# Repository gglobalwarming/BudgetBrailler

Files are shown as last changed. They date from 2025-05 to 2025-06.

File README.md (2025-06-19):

# BudgetBrailler
Open source, open hardware, low-cost electric brailler. This project is a work in progress, although I have produced (mostly) working prototypes which make very nice braille dots. I am a biologist not an engineer of any sort so I'm sure there are many improvements to be made. Any feedback to improve the design would be appreciated!  

## Introduction
Braillers (aka Braille typewriters) are used by Blind or Visually Impaired persons to produce written text that can be "read" by touch based on patterns of dots. These devices can range from ~$800 for a mechanical Perkins Brailler to thousands of dollars for electric braillers. Having built several 3D printers from kits I wanted to see if I could design a low-cost brailler for a similar price to an entry level 3D printer. The  basic functional design is a set of rollers turned by a stepper motor to feed paper in and out, a toolhead on a linear rail driven by a stepper motor through a belt to move across lines of the paper, a linear actuator to imprint the dots on the page, and a keyboard for user input.  

## Design Goals
* The embosser should cost $100-200. My original inspiration for this project was that if you can buy or build a capable 3D printer for that price, you should be able to do the same with a braille embosser.  
* The embosser should be open source and open hardware.  
* The embosser should be entirely 3D printed or made with off-the-shelf components.  
* The embosser should be simple. There should be as few parts as possible and, except for the electronics, no complex mechanisms.  
* The embosser should have an optional case to protect the user and the embosser.  
* The embosser should be well documented. This includes a bill of materials, detailed instructions, code, wiring diagrams, and stl and CAD files for all printed parts.  

## Limitations
* Custom keyboard  
* Feeding paper is imprecise  
* Manually aligning first line on page required  
* Printing parts requires 256mm print bed  
* Long term durability not tested  
* Very little auditory feedback  
* Manual wiring and crimping needed
* No screen for high vision users

## Future Improvements:
* Implement user feedback. Please let me know any problems or suggestions you have!  
* Learn FreeCAD and remake all the 3D printed parts to move away from SolidWorks  
* Write code to allow the embosser to accept braille ASCII files to print  
* Implement QWERTY keyboard compatibility  
* Redesign custom keyboard to have its own microcontroller and memory  
* Allow keyboard to be used separately as a note taker then later connected for printing  
* Implement more auditory feedback from embosser  
* Detect when paper reaches the print line  
* Improve paper feeding more generally  
* Make 3D printable gears as an option  
* Search for alternative electronics which are simpler, less expensive, or more reliable  
* Design PCBs to reduce wiring complexity  
* Design alternate print heads to make different size dots
* Invert printing so that braille can be read right-side up without removing paper
* Add optical snsor to auto-align page for first line printing  
* Test different linear actuators  

## Similar Projects
There are several similar open source braillers, although they are directed at printing from files rather than being used like a typewriter. The top two are linked below:  
[BrailleRap](https://www.braillerap.org/en/)  
[OpenBraille](https://github.com/carloscamposalcocer/OpenBraille)

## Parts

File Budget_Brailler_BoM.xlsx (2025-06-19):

Name | Other Name/Notes | Quantity | Cost/Unit | Cost | Link
Total |  |  |  | 185.4533333
3D Printing |  |  |  | 30
Filament | ~1kg PLA/PETG/ABS, ~15g TPU | 1.5 | 20 | 30
Electronics |  |  |  | 81.63333333
Buck Converter | LM2596 | 1 | 1.3 | 1.3 | https://www.amazon.com/gp/product/B0DBVWQGZL/ref=ppx_yo_dt_b_asin_title_o00_s01?ie=UTF8&psc=1
Stepper Motor | XY42STH34-0354A | 2 | 14 | 28 | https://www.adafruit.com/product/324
NC End Stop | ThTRht B0CB85485W | 1 | 0.2 | 0.2 | https://www.amazon.com/dp/B0CB85485W?ref=ppx_yo2ov_dt_b_fed_asin_title&th=1
Mosfet Driver | RFP30N06LE N-Channel Power MOSFET | 1 | 0.8 | 0.8 | https://www.adafruit.com/product/5648
S2 Mini | Adafruit MOSFET Driver - For Motors, Solenoids, LEDs, etc - STEMMA JST PH 2mm | 1 | 4 | 4 | https://www.amazon.com/dp/B0CKLGGNKY?ref=ppx_yo2ov_dt_b_fed_asin_title
Motor Drivers | TB6612 | 2 | 7 | 14 | https://www.adafruit.com/product/2448
12V Linear Actuator | TAU1040T-07 | 1 | 15 | 15 | https://www.adafruit.com/product/413
Perma-Proto Board | Perma-Proto Quarter-sized Breadboard PCB (better solutions likely exist, I am just using it for common ground/power) | 1 | 2.833333333 | 2.833333333 | https://www.adafruit.com/product/589
Power Jack | Panel Mount 2.1mm DC barrel jack | 1 | 3 | 3 | https://www.adafruit.com/product/610
Piezo Buzzer | PS1240 | 1 | 1.5 | 1.5 | https://www.adafruit.com/product/160
12V Power Supply | I'm currently using a 12V 5amp power supply with a 2.1mm barrel jack. I doubt this uses the full 5 amps so I will update this once I test that. | 1 | 10 | 10 | https://www.amazon.com/Facmogu-Transformers-100-240V-Converter-Available/dp/B0BYVK73BP
Wire | If you're doing your own wiring. |  |  | 1
Connectors / crimping tools | If you're wiring your own connectors you'll need the appropriate connectors and tools.
Keyboard |  |  |  | 19.6
1N4007 Diode |  | 14 | 0.15 | 2.1 | https://www.adafruit.com/product/1641
Keys | CherryMX size | 14 | 0.5 | 7 | https://www.adafruit.com/product/4955
Keycaps | CherryMX size | 14 | 0.5 | 7 | https://www.adafruit.com/product/4997
Switch Sockets | Kailh Switch Sockets for MX-compatible Mechanical Keys - 20 Pack | 14 | 0.25 | 3.5 | https://www.adafruit.com/product/4958
Motion |  |  |  | 49.22
Bearing | F695rs Bearings | 2 | 0.95 | 1.9 | https://www.amazon.com/dp/B09YLDL5WK?ref_=ppx_hzod_title_dt_b_fed_asin_title_1_4
Belt | 2GT-6 Width | 0.5 | 9 | 4.5 | https://www.amazon.com/dp/B0BVJSRD6F?ref=ppx_yo2ov_dt_b_fed_asin_title
Idler | 5mm Bore 20 Teeth Suitable for 6mm Belt | 1 | 1 | 1 | https://www.amazon.com/dp/B07J4JC2N7?ref=ppx_yo2ov_dt_b_fed_asin_title
250mm Linear Rail | MGN12 250mm Linear Rail Guide with MGN12H Linear Bearing Carriage Block | 1 | 18 | 18 | https://www.amazon.com/dp/B09QPP35N1?ref=ppx_yo2ov_dt_b_fed_asin_title
Pulley | GT2 Pulley 20 Teeth 5mm Bore | 1 | 1.32 | 1.32 | https://www.amazon.com/dp/B0CPYN865G?ref=ppx_yo2ov_dt_b_fed_asin_title
Linear Rod | 5mm x 300mm linear rod | 2 | 5 | 10 | https://www.amazon.com/dp/B0CXVB6G3D?ref=ppx_yo2ov_dt_b_fed_asin_title&th=1
Motor Gear | 32P 20T Pinion Gear Mod 0.8, 5mm shaft (ProtekRC PTK-8063 is the one I used) | 1 | 4.5 | 4.5 | https://www.amainhobbies.com/protek-rc-steel-32p-pinion-gear-w-3.17mm-reducer-sleeve-mod-.8-5mm-bore-20t-ptk-8063/p735082?v=704112&gad_source=1
Roller Gears | 32P 27T Pinion Gear Mod 0.8, 5mm bore (Traxxas 5647 are the ones I used) | 2 | 4 | 8 | https://www.amainhobbies.com/traxxas-32p-hardened-steel-pinion-gear-w-5mm-bore-27t-tra5647/p454505?v=746125
Fasteners | Note: I think all the amounts here are correct. Having spares will never hurt. |  |  | 5
M2 Screws | M2x10 minimum, M2x20 maximum. Exact length not critical | 6
M2x10 Self-Tapping Screws | Used for mounting the end stop | 2
M2 Nuts |  | 6
M3x8 Screws |  | 20
M3x12 Screws |  | 19
M3x18 Screws |  | 8
M3x25 Screws | Note: you can also use another M3x30 screw and an extra M3 nut in place of this screw | 1
M3x30 Screw |  | 6
M3 Nuts |  | 21
M5x16 Screw |  | 1
M5 Nut |  | 1

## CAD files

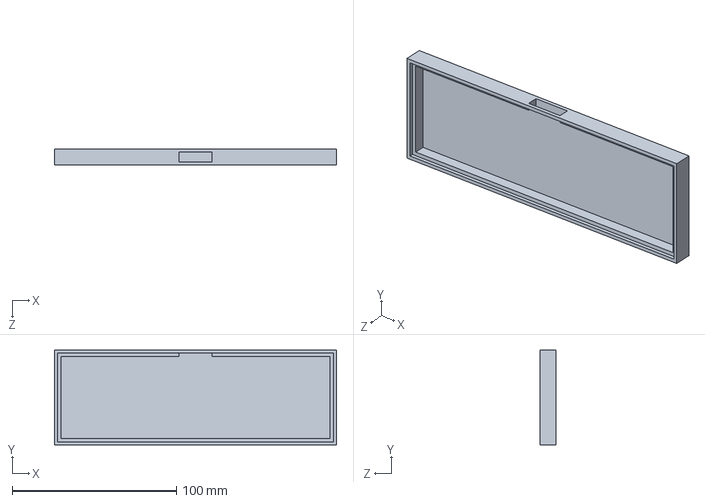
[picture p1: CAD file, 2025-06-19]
BB_Keyboard/BB_Keyboard_Bottom.SLDPRT
171.8 x 57.8 x 10.0 mm

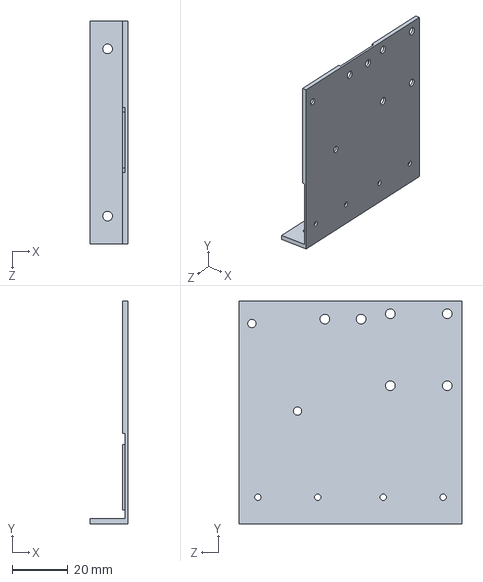
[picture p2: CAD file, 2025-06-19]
BudgetBrailler_Solidworks/BB_Electronics_Mount1.SLDPRT
13.6 x 80.0 x 80.0 mm

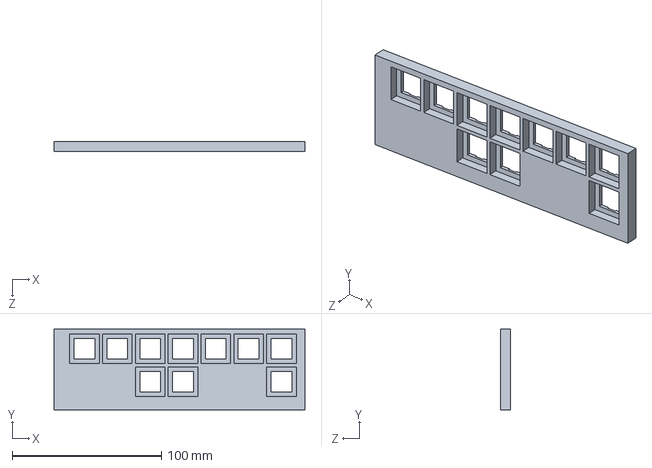
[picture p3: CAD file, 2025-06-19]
BB_Keyboard/BB_Keyboard_Top.SLDPRT
168.2 x 54.2 x 7.00 mm

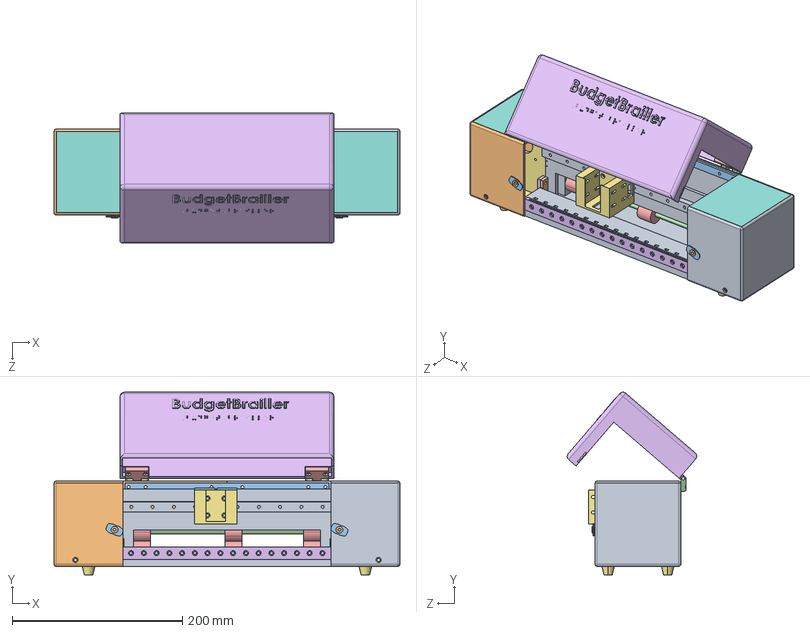
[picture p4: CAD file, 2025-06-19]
BudgetBrailler_Solidworks/BudgetBrailler.STEP
406.8 x 214.8 x 152.3 mm
BB_Middle
BB_Right_Side
BB_Left_Side
BB_Right_Casing
BB_Left_Casing
BB_Back_Brace
BB_Hinge_Outer x 2
BB_Hinge_Inner x 2
BB_Lid
BB_Carriage
BB_Belt_Clamp x 2
Linear_Rail
BB_Cam_Mount x 2
BB_Cam_Latch x 2
Rod_5x300mm x 2
BB_Roller_Gripper x 6
BB_Channel
BB_Foot x 4
BB_CB_Mount

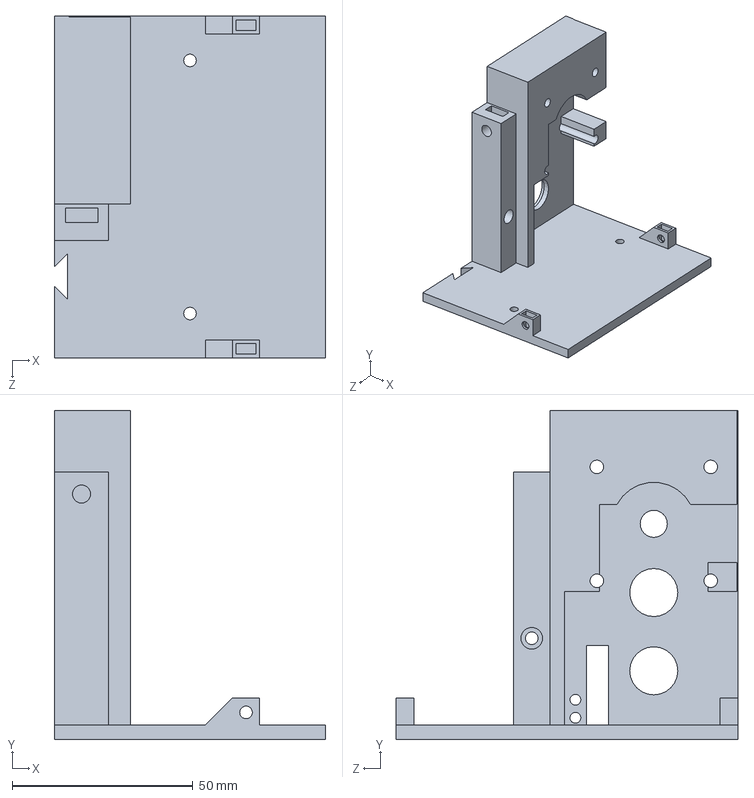
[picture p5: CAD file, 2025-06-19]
BudgetBrailler_Solidworks/BB_Right_Side.SLDPRT
75.0 x 91.0 x 94.5 mm

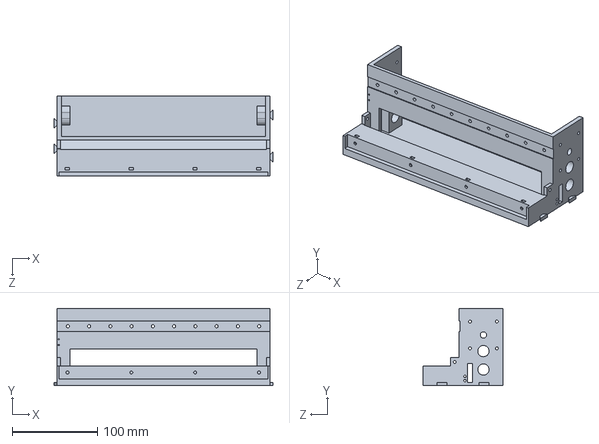
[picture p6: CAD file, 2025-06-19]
BudgetBrailler_Solidworks/BB_Middle.SLDPRT
257.5 x 91.0 x 94.5 mm

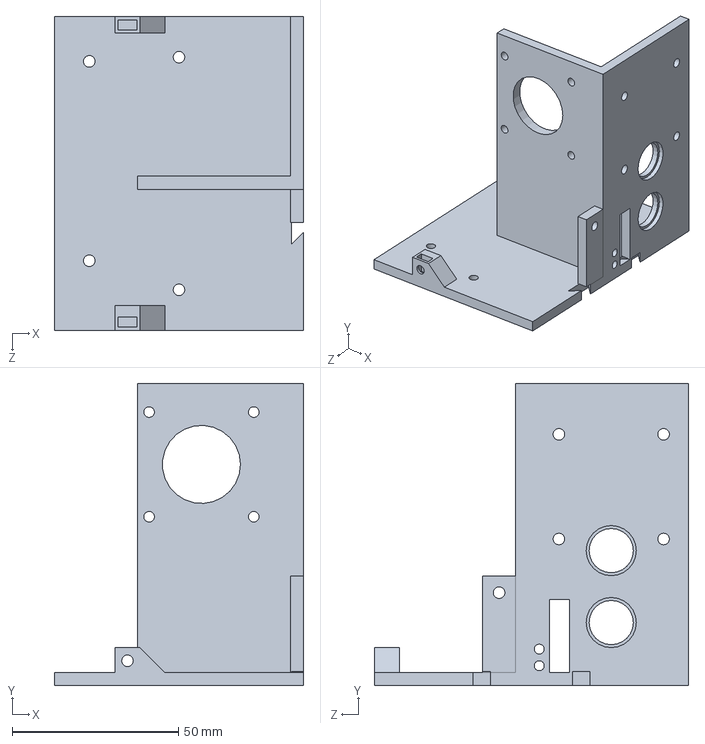
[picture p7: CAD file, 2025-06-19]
BudgetBrailler_Solidworks/BB_Left_Side.SLDPRT
75.0 x 91.0 x 94.5 mm

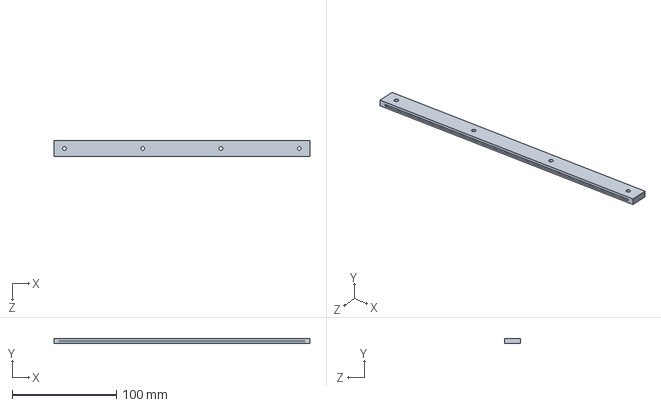
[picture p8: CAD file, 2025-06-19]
BudgetBrailler_Solidworks/BB_Channel.SLDPRT
245.4 x 5.00 x 15.0 mm

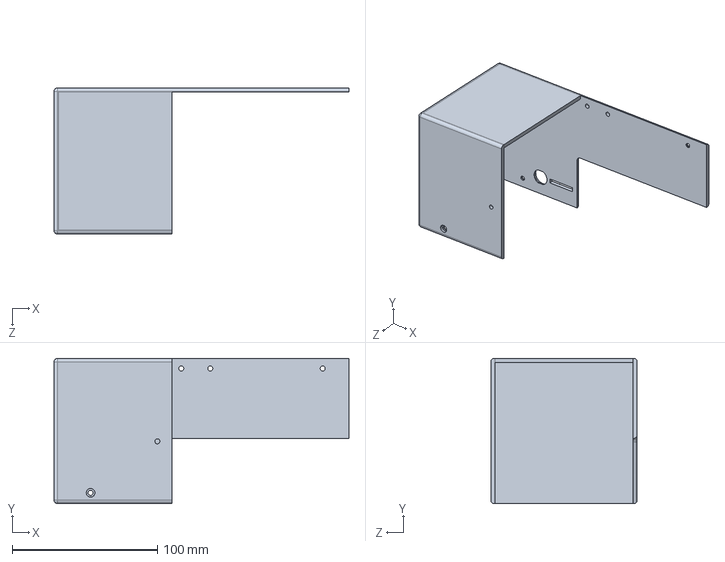
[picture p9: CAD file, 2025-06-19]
BudgetBrailler_Solidworks/BB_Left_Casing.SLDPRT
203.3 x 100.2 x 100.9 mm

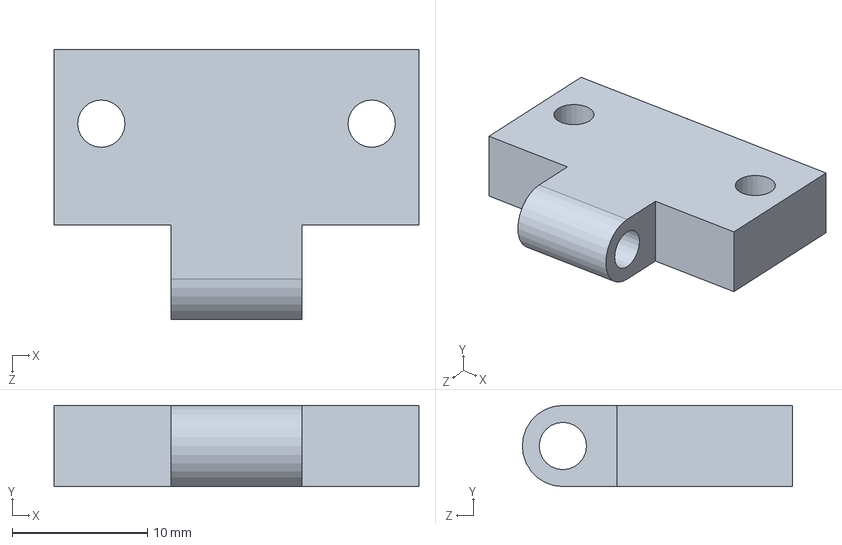
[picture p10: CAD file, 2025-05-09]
BudgetBrailler_Solidworks/BB_Hinge_Inner.SLDPRT
27.0 x 6.00 x 20.0 mm

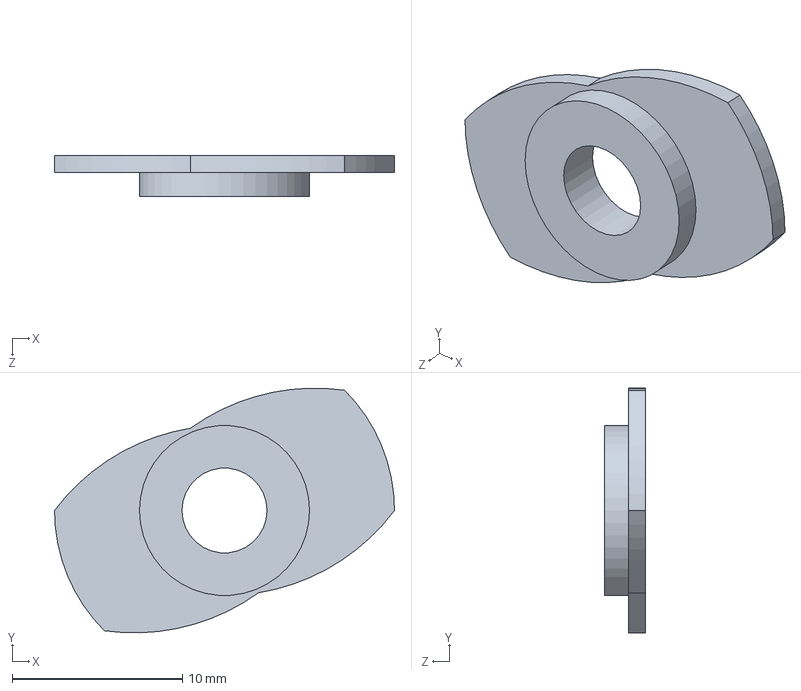
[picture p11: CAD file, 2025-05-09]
BudgetBrailler_Solidworks/BB_Cam_Latch.SLDPRT
20.0 x 14.4 x 2.40 mm

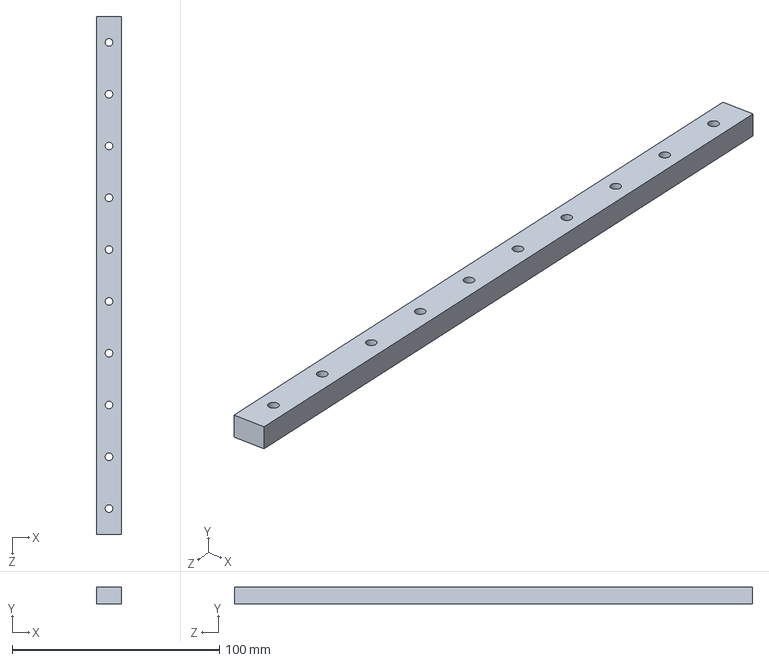
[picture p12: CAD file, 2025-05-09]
BudgetBrailler_Solidworks/Linear_Rail.SLDPRT
12.0 x 8.00 x 250.0 mm

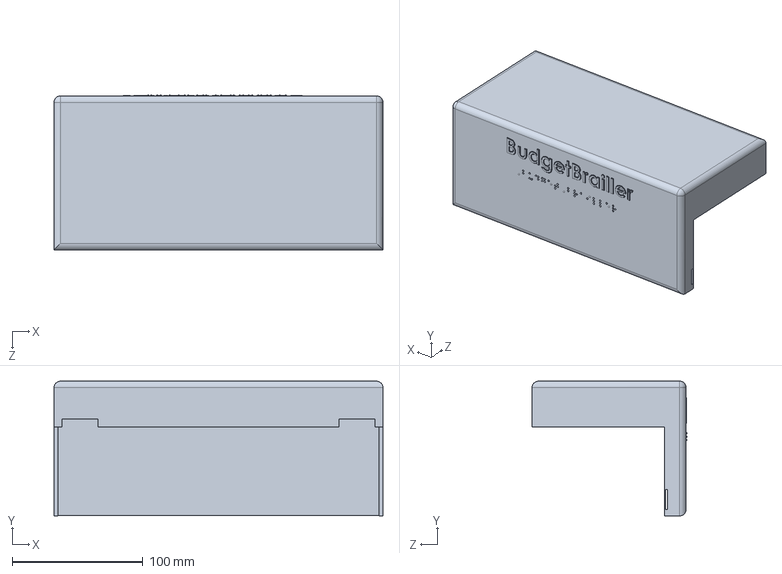
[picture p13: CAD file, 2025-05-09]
BudgetBrailler_Solidworks/BB_Lid.SLDPRT
251.4 x 103.0 x 118.4 mm

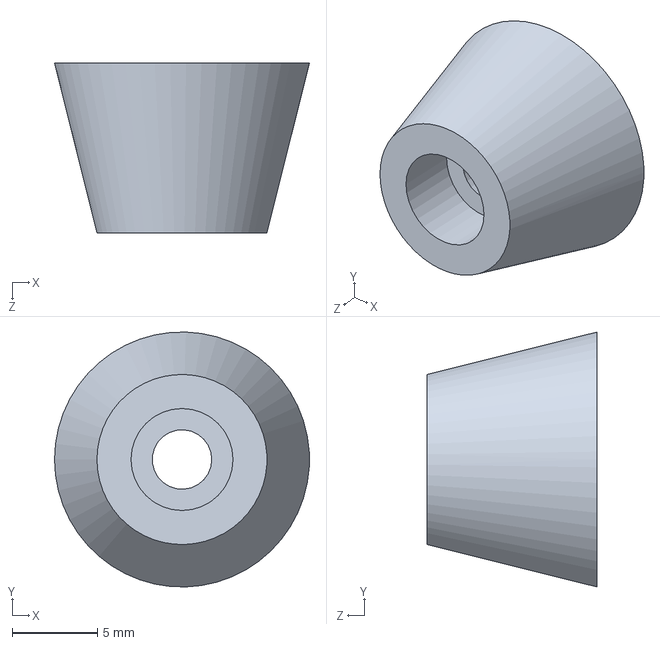
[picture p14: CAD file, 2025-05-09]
BudgetBrailler_Solidworks/BB_Foot.SLDPRT
15.0 x 15.0 x 10.0 mm

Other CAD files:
BudgetBrailler_Solidworks/BB_Belt_Clamp.SLDPRT
BudgetBrailler_Solidworks/BB_Roller_Gripper.SLDPRT
BudgetBrailler_Solidworks/BB_Carriage.SLDPRT
BudgetBrailler_Solidworks/BB_Hinge_Outer.SLDPRT
BB_Keyboard/BB_Keyboard_Bottom.STL
BB_Keyboard/BB_Keyboard_Top.STL
BudgetBrailler STLs/BB_Back_Brace.STL
BudgetBrailler STLs/BB_Belt_Clamp.STL
BudgetBrailler STLs/BB_CB_Mount.STL
BudgetBrailler STLs/BB_Cam_Latch.STL
BudgetBrailler STLs/BB_Cam_Mount.STL
BudgetBrailler STLs/BB_Carriage.STL
BudgetBrailler STLs/BB_Channel.STL
BudgetBrailler STLs/BB_Electronics_Mount1.STL
BudgetBrailler STLs/BB_Foot.STL
BudgetBrailler STLs/BB_Hinge_Inner.STL
BudgetBrailler STLs/BB_Hinge_Outer.STL
BudgetBrailler STLs/BB_Left_Casing.STL
BudgetBrailler STLs/BB_Left_Side.STL
BudgetBrailler STLs/BB_Lid.STL
BudgetBrailler STLs/BB_Middle.STL
BudgetBrailler STLs/BB_Right_Casing.STL
BudgetBrailler STLs/BB_Right_Side.STL
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

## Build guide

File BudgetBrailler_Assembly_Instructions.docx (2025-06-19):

BudgetBrailler Assembly Instructions

https://github.com/gglobalwarming/BudgetBrailler

NOTE: Assembly instructions are currently for a previous version. There have only been small changes, but I will remake the instructions soon with updated pictures, parts, and instructions.

Printed Parts:

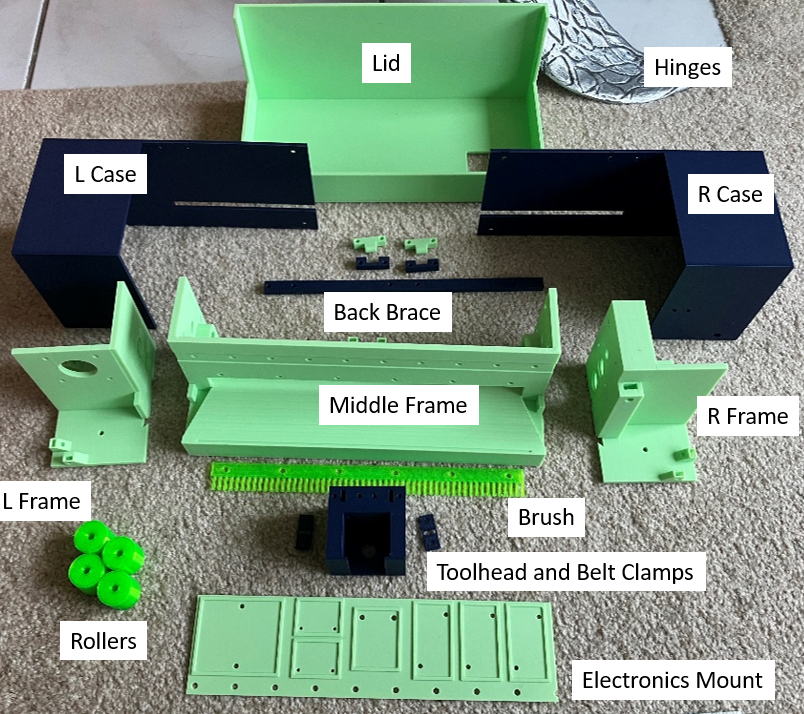
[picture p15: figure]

Parts to print in TPU:

- 4x Rollers: Cylinders 22mm in diameter and 20mm in length with a 5mm bore through the center. These are put on the linear rods and are used to grip the paper.
- 4x Feet: Conical pieces 10mm tall with 15mm and 10mm diameter ends a bore through the center for an M3 screw and nut. Used to reduce noise during printing and protect the surface the printer is on. Not present in the picture because I forgot to print them ahead of time.

Required parts printed in PLA/PETG:

Note: I printed mine out of PLA because I have been actively redesigning parts and wanted to more easily reprint parts as I iterated. As is always the case with FDM printing, PLA will be less durable and UV sensitive so ideally the parts should be printed from a different material (in this case PETG is probably the most sensible choice). Note: the “ramps” that are described below exist to allow printing of M3 nut mounts without supports. They do not serve any other function in the printer.

- 1x Left Frame: Contains the x-motor mount as well as spaces for the left bearings. Rectangular base 65mm wide by 95mm long. On the base are 4 ramped structures 15mm wide by 7.5mm long by 7.5mm with space for M3 nuts. These are used for mounting the case to the frame. Rising from the base is a backwards L-shaped wall 87mm tall with one leg near the center of the base and the other on the far-right side extending to the back. Near the top, the front wall has four holes for M3 screw and a larger 25mm hole in the middle. These holes are used to mount the x-axis motor and allow the shaft the pass through to the front of the embosser. On the right side of the L-wall near the top are four holes for M3 screw for connecting the left frame to the middle frame. Below that are two sets of holes ~15mm in diameter for the bearings. These wholes have a larger, shallower hole around a slightly smaller deeper hole to accommodate the shape of the bearings. Just in front of the L-wall on the right side is a raised piece with an M3 screw hole on it as another point to attach to the middle frame. On the bottom of the left frame on the right side are two ~10mm dovetail cutouts that connect to the middle frame. On the bottom are also two M3 screw holes for mounting the TPU feet.
- 1x Middle Frame:
- 1x Right Frame: Contains space for the roller motor as well as spaces for the left bearings and a mount for the belt idler. Close to a mirror image of the left frame with the following differences: No holes for an x-axis motor, additional hole in the center of the four screw holes that connect to the middle frame to provide space for the roller motor shaft, spacer extending around those same four screw holes to provide space between the roller motor and the wall, the piece holding the front screw hole to connect to the middle piece extends upward about 60mm where it has an M5 screw hole and space for an M5 nut to mount the belt idler.
- 1x Toolhead: Attached to the linear rail on the middle frame. Holds the linear actuator and move in the x-axis of the embosser. ~50mmm cube with a large cutout in the front/middle for the linear actuator. At the back is a cutout to fit onto the carriage of the linear rail as well as a cutout for the belts to pass through. Four M3 screw/nut holes go through the toolhead vertically near the back to mount the belt clamps as well as rectangular holes for the belt to pass through.
- 2x Belt Clamp: Attached to the top of the toolhead to hold the belts in place. Rectangular pieces 25mm by 10mm by 2mm with two holes for M3 screws and a rectangular hole for the belt to go through.
- 1x Electronics Mount: Attached to the middle frame behind middle wall and used to hold electronic components in place. Rectangular piece about 230mm by 55mm by 1mm with a row of 9 holes for M3 mounting screws at the bottom. On the front are a series of raised outlines for the various electronic components with holes for M3 or M2 screw to hold each part in place. From left to right (the largest outline should be on the far left): Solderable prototype board above the first three mounting screw holes, two motor drivers both above the fourth mounting screw hole, ESP-32 S2 Mini microcontroller above the fifth and sixth mounting screw holes, LM2596 buck converters for converting the 12V input power to the 5V needed to power the microcontroller above the seventh set of screw holes. To the right of these is 65mm of empty space which could be used in the future for mounting additional components.
- 1x Embosser: A 10mm diameter base, 3.5mm top cone with a small raised dot on one the small end of the cone the size of a braille dot and the other end of the cone hollow. Friction fits onto the end of the linear actuator with the hollow end and is used to emboss the braille dots. Not pictured because I forgot to print it ahead of time.
- 1x Keyboard Bottom: An open topped box 167mm by 53mm by 20mm with six screw and nut holes for M3 screws to hold the electronics and Keyboard Top to the bottom of the keyboard. Has a 2mm cutout on the top for the Keyboard Top to snap into place. Has a 20mm by 6mm hole at the back for cables to pass through.
- 1x Keyboard Top: 163mm by 63mm by 9mm box with two cutouts for M3 screws to connect to the Keyboard Bottom and 10 slots for MX Cherry keyboard keycaps.
- Left Case:
- Right Case: a mirror image of the left case.
- Lid:
- Back Brace:
- 2x Hinge Outer:
- 2x Hinge Inner:

Purchased Components:

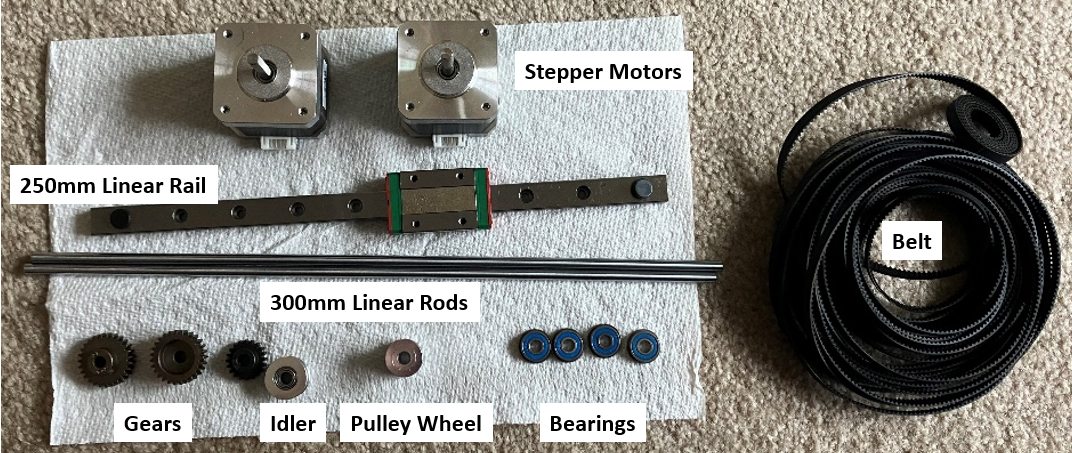
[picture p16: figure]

- 2x Stepper Motor: 42mm x 40mm stepper motors to drive the x-axis and rollers. Cube roughly 40mm/side. Near the bottom on one side face is a plug with six pins for plugging in a cable. On the top are four M3 screw holes for mounting the motor, a round 1mm by ~20mm raised ring with a 5mm shaft in the center. The shaft has one side flattened to allow a set screw to grip better.
- 1x 250mm Linear Rail: The toolhead will be mounted on the carriage of this linear rail to allow it to move on the x-axis. A metal rectangular piece 250mm by 5mm by 3mm with 10 holes for M3 mounting screws. On the a 40mm by 20mm rectangular carriage which slides along the rail. In the two outermost screw holes are rubber caps which prevent the carriage from sliding off and spilling the ball bearings inside it all over the place.
- 3x Gears: These gears come in two sizes. One is slightly smaller and will be attached to the roller motor shaft. The other two are slightly larger and will go on each of the two linear rods. The three gears will mesh in a vertical line in the order: Motor>Top Rod>Bottom Rod. Therefore, when the motor turns in one direction, the top rod will turn in the opposite direction and the bottom rod will turn in the same direction. For example: motor turning clockwise, top rod turning counterclockwise, bottom rod turning clockwise. Because the rollers on the top rod will be gripping the top of the paper and the bottom rod the bottom of the paper, the opposing directions of rotation will result in both rods pushing the paper in the same direction.
- 1x Idler: Placed on the opposite end of the linear rail from the x-axis motor and will allow the belt to loop back to the toolhead. A metal cylinder with a bearing in the middle and a 5mm bore. Around the outside of the cylinder are teeth to mesh with the belt.
- 1x Pulley Wheel: Attached to the x-axis motor to drive the belt. Metal cylinder with teeth on the outside to mesh with the belt. There are two holes 90° apart from one another on the rounded side for the threading of set screws to hold the pulley wheel on the motor shaft.
- 4x Bearings: Used to allow the rods to rotate freely while being held in place. Round metal pieces ~20mm in diameter with a 5mm bore. The center section can rotate freely.
- 1000mm (1m) Belt: Used to move the toolhead along the x-axis. 6mm wide plastic belt flat on one end and with teeth on the other. Embedded in the belt are strands of wire to provide added strength. Actual length used will be closer to 750mm.

Fasteners

M2 Screws (M2x10 minimum, M2x20 maximum) | 6
M2x10 Self-Tapping Screws | 2
M2 Nuts | 6
M3x8 Screws | 20
M3x12 Screws | 19
M3x18 Screws | 8
M3x25 Screws | 1
M3x30 Screw | 6
M3 Nuts | 21
M5x16 Screw | 1
M5 Nut | 1

Frame Assembly:

In this section we will assemble the main frame of the embosser. As part of the that assembly we will also mount most of the components to the frame.

1. Insert bearings into the holes on the sides of the Left and Right Frames. The fit should be tight and the bearings should snap securely into place. The bearings should sit roughly flush with the wall of the once they are inserted.

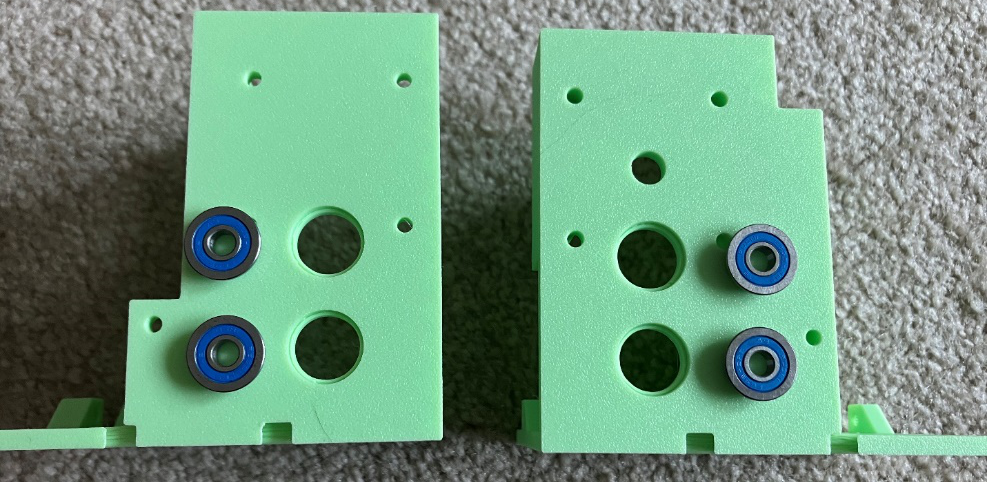
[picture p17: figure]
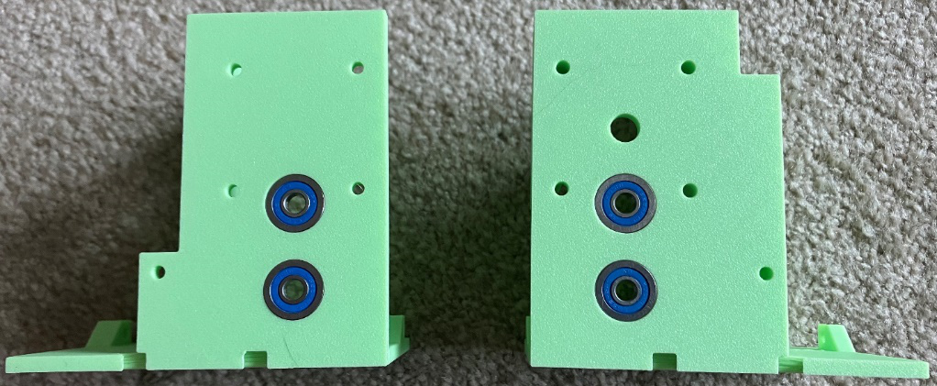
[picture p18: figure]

2. Connect the Left and Right Frames to the Middle Frame using the dovetails on the bottom. The wall running near the center of each of the frames should be colinear. If the walls are out of alignment you probably have the left and right segments swapped. The dovetails should be tight but can be removed if you made a mistake. The bottom of the frames do not need to be perfectly flush as connecting screw between the pieces will secure the frame.

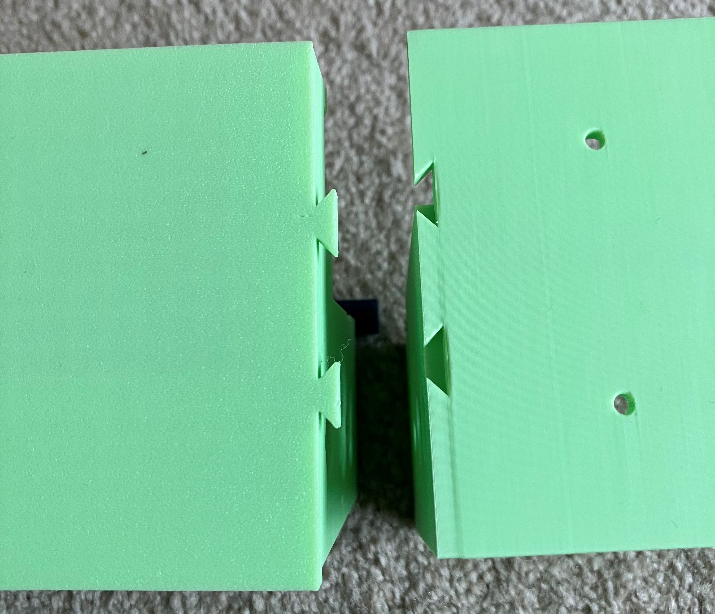
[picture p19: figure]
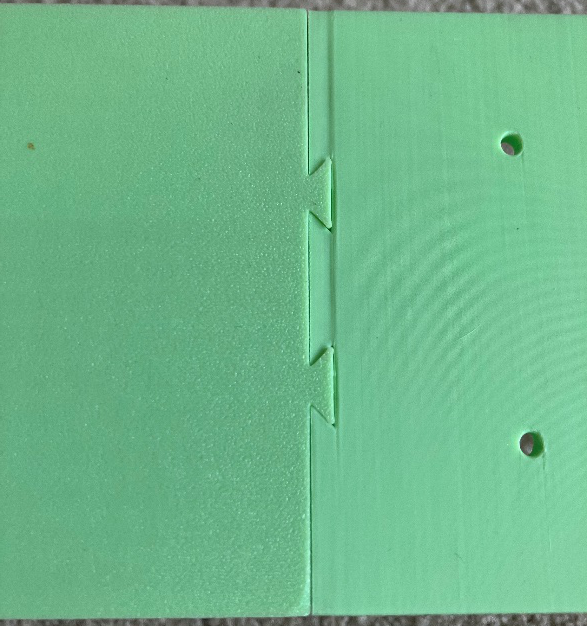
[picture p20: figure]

3. Attach the 3d printed feet to the bottom of the left and right frames with four M3x12 screws and four M3 nuts. There is space for a M3 nut to be trapped on the bottom side of the feet and a screw can be inserted from the top side of the frame.

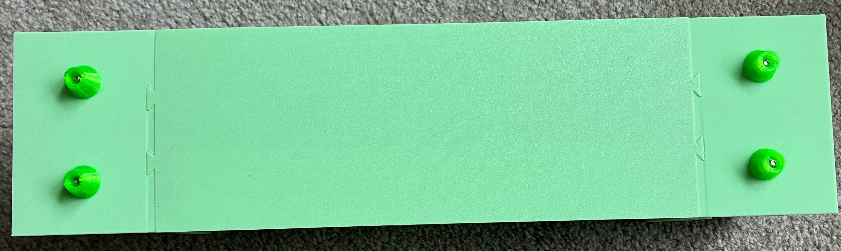
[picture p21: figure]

4. At the front of the frame, connect the Left Frame to the Middle Frame using the screw hole just in front of the middle wall using an M3x12 screw and an M3 nut.
5. At the front of the frame, connect the Right Frame to the Middle Frame using the screw hole just in front of the middle wall using an M3x25 screw and an M3 nut. Note: you can also use an M3x30 screw with an M3 nut put on by the head of the screw as a spacer. This reduces the number of different screws you need.
6. At the back of the frame, connect the Left Frame to the Middle Frame using the four screw holes on the parallel walls with four M3x12 screws and four M3 nuts

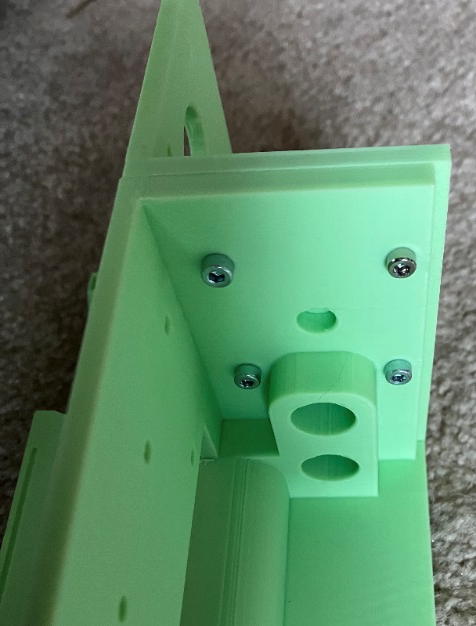
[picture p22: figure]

7. Attach the 32P 20T Mod 0.8, 5mm shaft Pinion Gear to one of the stepper motors by sliding it onto the shaft with the teeth farther from the motor body about 8mm from the end of the shaft. Align the set screw with the flat side of the shaft and tighten the screw. You should now be able to rotate the gear and shaft together without the pulley slipping. This will be the roller motor.
8. Orient the motor so the plug is oriented up. At the back of the frame, attach the roller motor to the top of the Right Frame (which will currently be on the left side of the frame since you are looking at it from the back) using four M3x30 screws. The screws will go into the four holes near the top on the left side (while looking at the frame from the back) of the Middle Frame, go through the thick wall on the Right Frame, and thread into the holes on the motor. Check to make sure the plug on the motor is still facing up. You may need to adjust the positioning of the pulley on the motor shaft. You can access the gear and its set screw from below. The gear should be close to the wall but ideally not touching the wall. The other gears will be larger so the exact placement of this gear is not critical to ensure that the gears mesh.

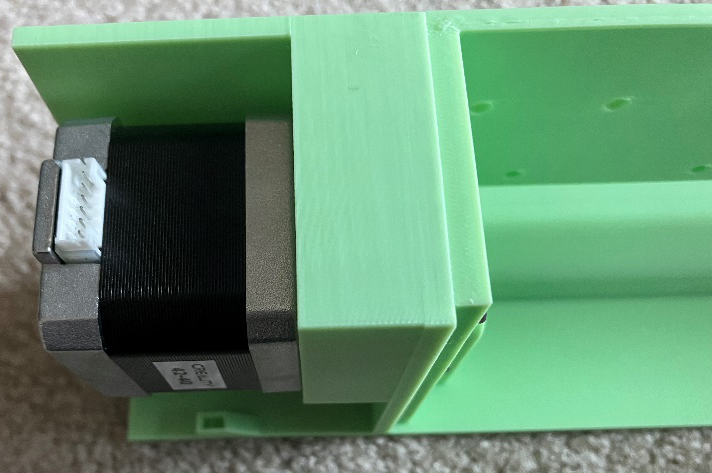
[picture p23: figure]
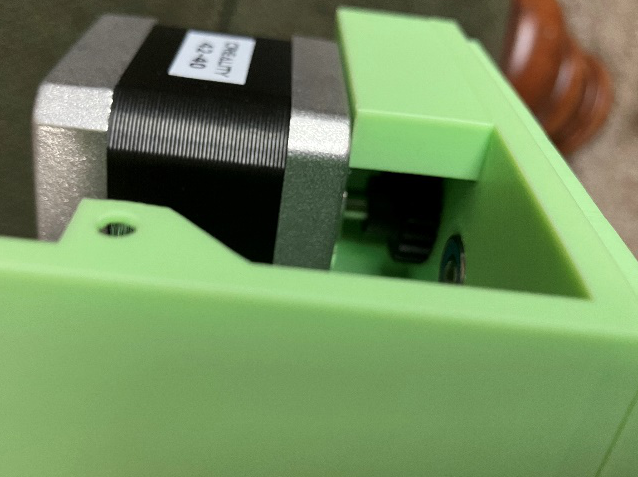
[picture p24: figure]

9. From the back of the frame, insert the linear rods through the bearing on the Left Frame (currently on the right side as we are viewing the back of the frame) and about halfway through the Middle Frame. Slide two roller grippers onto linear rods, ensuring that there is at least 20mm between the grippers and that there is at least 30mm of rod sticking past the leftmost gripper. Note: The grippers will be VERY tight on the rod. Starting with the top rod, slide the linear rods through the bearing on the Right Frame (currently on the left side as we are viewing the back of the frame) and put a 32P 27T Mod 0.8, 5mm shaft Pinion Gear on the left end of the rod flush against the Right Frame wall. Adjust the rod so the end is flush with the end of the gear then tighten the set screw on the gear. The top rod gear and the motor gear should mesh with a little bit of wiggle room. While holding the rod gear in place against the Right Frame wall, push the closes roller gripper toward the gear as far as it will go. Repeat with the farther gripper but moving it away from the gear to the far side of the Middle Frame. The top rod should now be able to rotate but not move from left to right. Attach the gear and adjust the roller grippers on the bottom rod in the same way you did for the top rod. The bottom rod gear should mesh with the gears on the top rod and when you turn one gear the other should move smoothly in the opposite direction. Try feeding some braille paper or an index card through the rollers by manually turning one of the rollers to ensure that both sets of rollers grip the paper. Note: regular printer paper will not work well as it is too thin and tends to crumple.

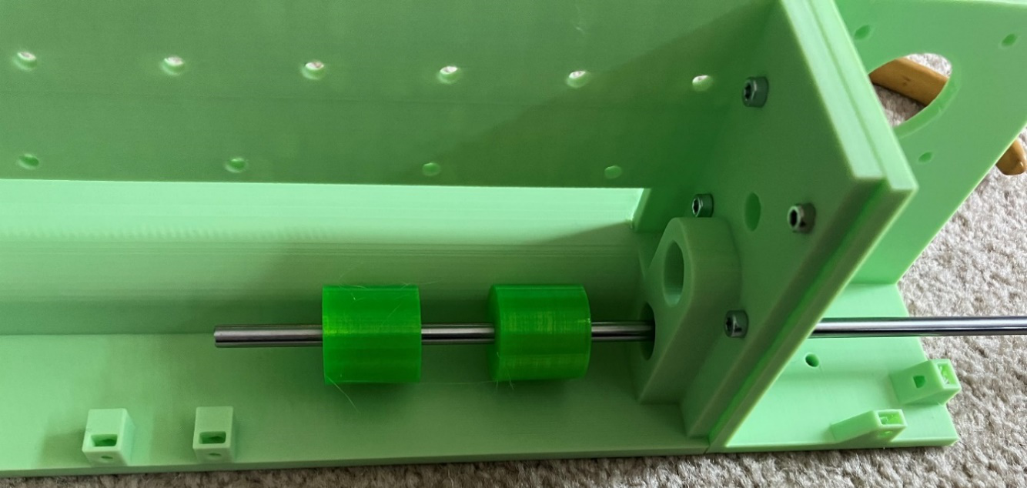
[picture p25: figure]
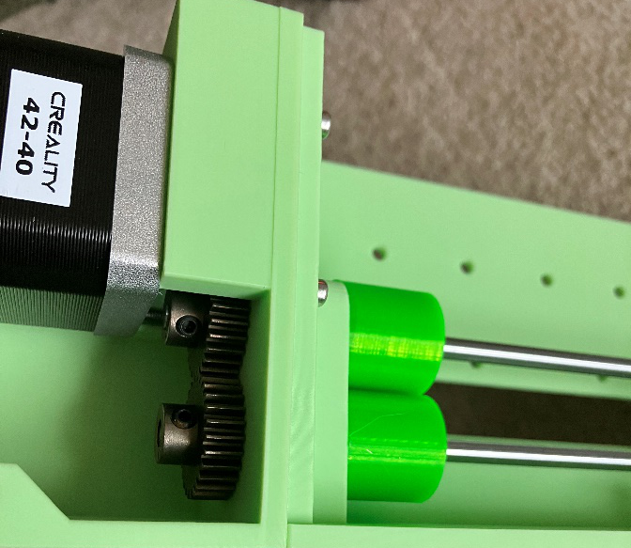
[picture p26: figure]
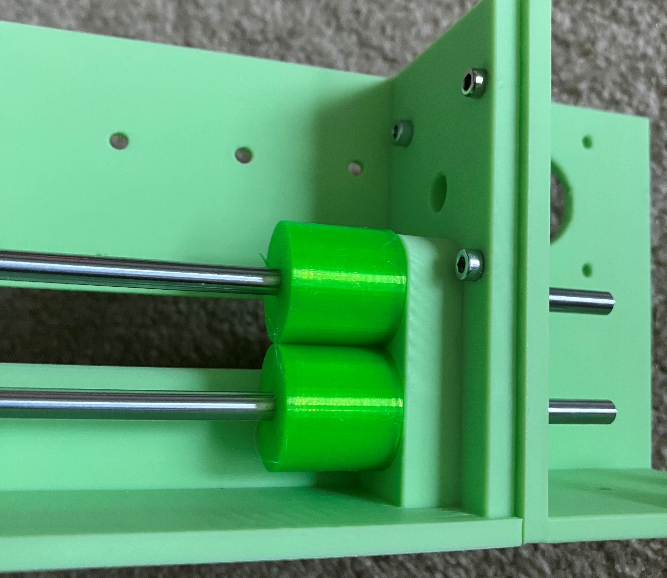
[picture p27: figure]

10. From the back of the left frame, put the second stepper motor (which will be the X motor) shaft through the large hole and screw it in place with four M3x8 screws. Put the pulley wheel on the shaft flush with the end of the shaft. Tighten the set screw against the flat edge of the shaft.

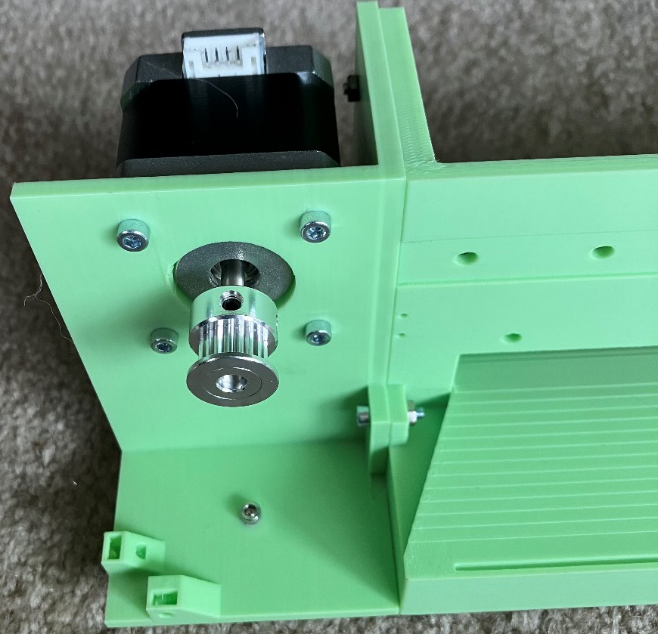
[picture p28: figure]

11. Attach the linear rail and brush to the front of the Middle Frame. Note: Do not take the rubber caps off the linear rail yet to prevent the carriage from sliding off. The linear rail goes in the inset channel near the top of the middle wall using between four and ten M3x16 screws and M3 nuts. Not every screw hole needs to be used although they can be; I found one on each end and two near the center seemed to work well. ~~The brush is attached below the linear rail with the “bristles” facing down using six M3x~~~~8~~ ~~screws and M3 nuts.~~ I removed the brush as it caused problems. Pictures will continue to include the brush until I take new ones.

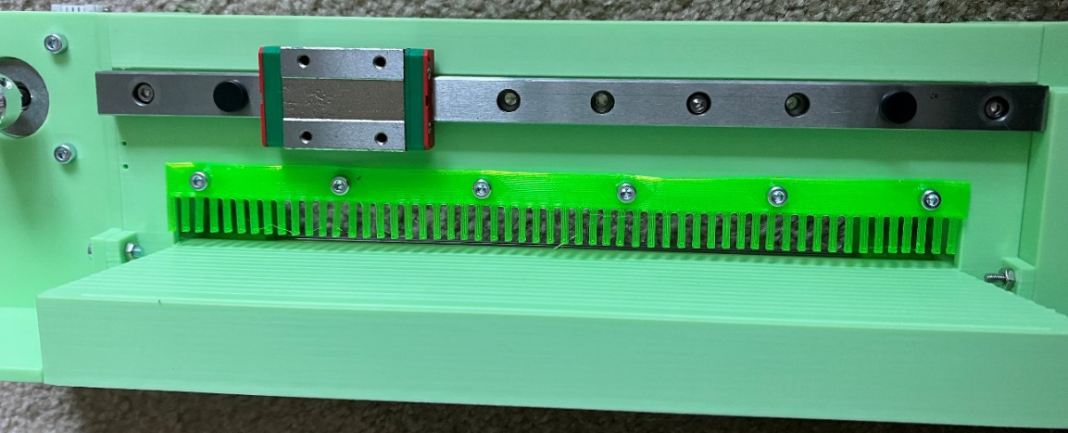
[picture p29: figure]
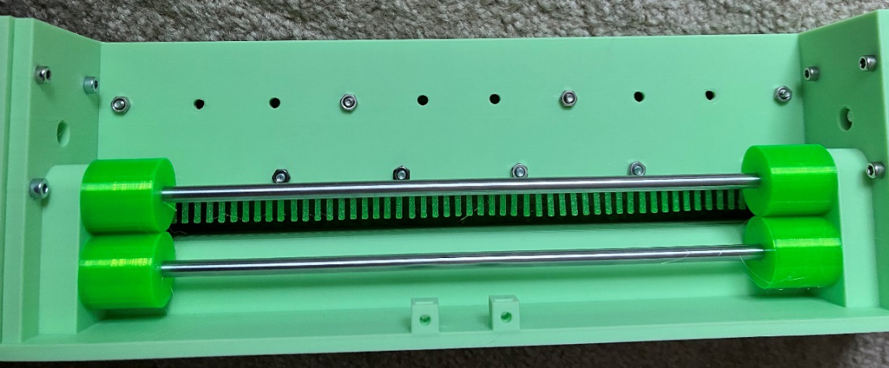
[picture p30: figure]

12. On the front of the Right Frame, insert an M5 nut into the hole at the top of the column just to the right of the linear rail. Put the idler onto an M5x16 screw and thread it through the hole into the nut. Adjust the tightness so the idler can just turn freely.

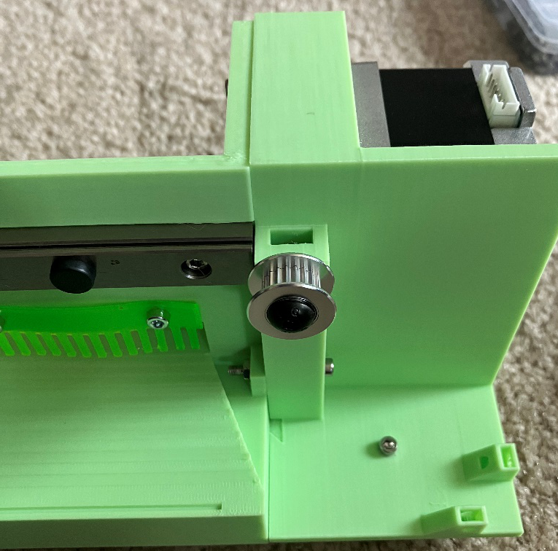
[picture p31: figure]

13. Screw the endstop into the two small holes to the left of the linear rail with M2x 10 self-tapping screws. The lever on the endstop should be facing upwards so that when the Toolhead moves to the left side of the rail it clicks the endstop. Once the end stop is mounted you can remove the rubber caps from the linear rail.
14. After mounting all the electronics on the Electronics Mount, secure the mount to the back middle of the printer using M3 nuts on the ends of the screws holding the linear rail. The electronics should facing the back of the printer and the Electronics Mount should be sticking up past the center wall.

Toolhead Assembly:

1. Insert an M3x16 or longer screw, through one the top holes in the Toolhead. Screw an M3 nut onto the end of it and tighten the nut. The nut will be pulled up into the hexagonal hole. Tighten the nut firmly to secure it in place then remove the screw. Repeat for the other three holes on the top of the Toolhead. The image below shows an example of a screw stuck through one of the holes with a nut on the end. Once the nut is tightened it will be pulled up until it is out of view and pulled tight against the plastic near the screw head.

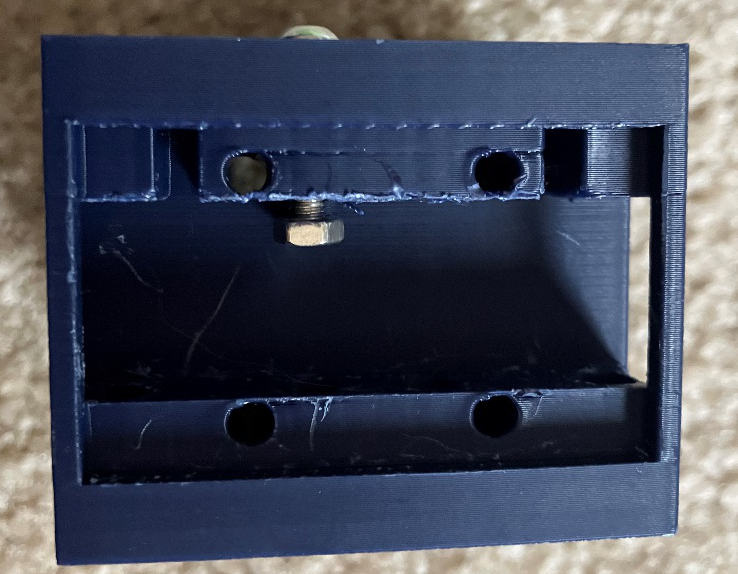
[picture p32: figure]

2. Loop the belt around the X-motor pulley with the teeth facing in. Hold one end of belt by the carriage (it doesn’t matter where on the linear rail the carriage is) and loop the other end idler and back to the carriage. The belt should now form a rough oval with the pulley on the left side, the idler on the right side, and both ends of the belt together at the top of the oval where the carriage is. Ensure you have ~30mm of extra length on each end of the belt and, if necessary, cut the belt to length. It’s better to have more than you need as you can always trim it later.
3. Remove the belt from the frame and run it through the back of the Toolhead in the same pattern. The teeth of the belt should always be facing the inside of the loop. Pass the two ends of the belt through the rectangular slots on the back of the Toolhead and out the top of the toolhead with about 20mm of length sticking out the top. The teeth on the belts should be facing toward each other and the center of the Toolhead. Slide a Belt Clamp onto each end and tighten them to the trapped nuts placed in step 1 using M3x8 screws. You do not need to completely tighten these screws right now, just enough to keep the belts from sliding back out.

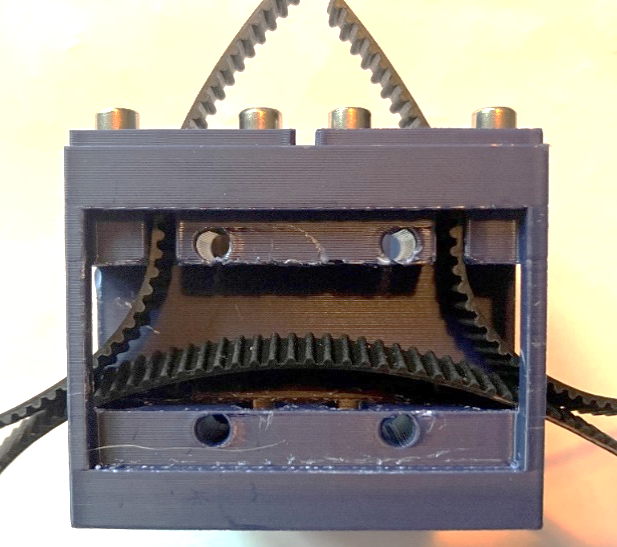
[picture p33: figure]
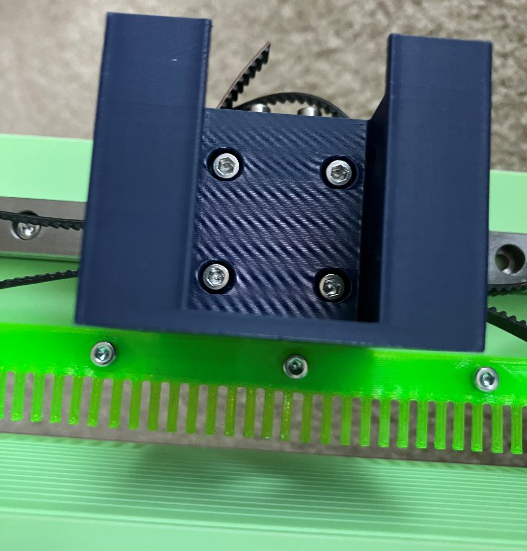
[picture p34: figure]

4. Screw the Toolhead with the round hole facing down onto the carriage with four M3x18 screws.
5. Loosen one of the two Belt Clamps (it doesn’t matter which one) and tighten the belt as tight as you can. While maintaining tension on the belt, tighten the Belt Clamp back down. The belt will still have some flex to it but should not be loose. If you pluck the belt, you will hear a soft twang. You should now be able to quickly and smoothly slide the toolhead from one end of the belt to the other without any slipping of the belt or binding of the carriage to the rail. The exact tension of the belt is not critical as long as the belt doesn’t slip.
6. Put the linear actuator into the Toolhead with the flat side of the plunger going through the hole in the bottom of the Toolhead. The actuator can be put in with the wires facing the back or the front and secured using the screw holes on the sides (there are holes on both sides but you will only use one set). Ideally the cable should be at the back of the toolhead so it is out of the way, but depending on how they coiled the wire there may not be space. Do not completely tighten the side screws as the position of the actuator will need to be adjusted later. SCREWS
7. Fit the Embosser onto the flat end of the linear actuator sticking below the toolhead. The fit will be very tight and the Embosser needs to be vertical. You can rotate the top of the linear actuator and feel the Embosser to see if the end of it is wobbling in a small circle. Adjust the positioning until the Embosser does not wobble.
8. Put a piece of paper under the Embosser and tap straight down on the linear actuator. Move the paper and repeat several times. If there is not a strong dot then loosen the screws holding the linear actuator in place and move it forward or backward as necessary. Repeat until you consistently produce dots that feel correct. With the screws at a particular tightness you should be able to slide the linear actuator with a little effort but have it stay in place otherwise, which makes this process easier. The tighter you can have the screws while testing the less chance that the alignment will change when you tighten them into their final position. Once you are finished tighten the screws and test the linear actuator again to make sure the alignment didn’t change when you tightened the screws. If necessary, repeat this process.

Case:

Consists of 8 parts: Left Case, Right Case, Lid, Back Brace, 2x Outer Hinge, 2x Inner Hinge.

1. Assemble the hinges by placing an Outer Hinge and an Inner Hinge their curved faces toward one another. The hole in the Inner Hinge curve surface will align with the two on the Outer Hinge curved surfaces. Insert an M3x30 screw through both hinge parts (passing through the Outer Hinge twice and the Inner Hinge once) and tighten an M3 nut on the end. The tightness of the nut can be adjusted later to match how stiff you want the lid to be.

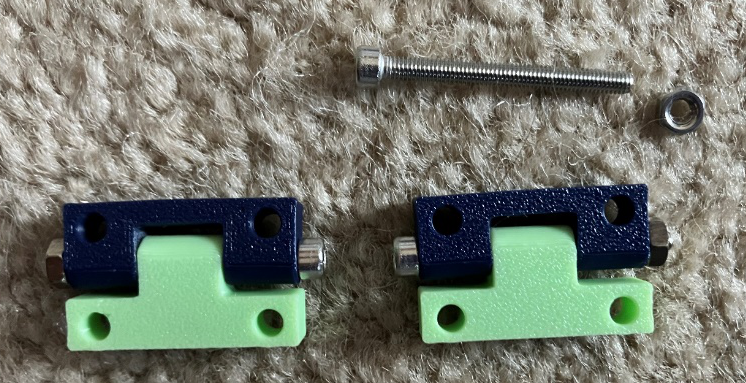
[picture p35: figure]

2. Align the Left Case and Right Case so that the long edges are colinear and the cutouts for the paper align with one another. The back wall of the case will have 6 screw holes (three on each half) in sets of two. These will align with the 6 holes on the Back Brace, which will go on the inside of the case. Attach the Back Brace to the Left Case and Right Case with two M3x10 screws and two M3 nuts in the center holes (one on each case segment). Using four M3x18 screws and four M3 nuts, attach Outer Hinges to the remaining four holes on the outside of the case with the Inner Hinge facing up. These screws will go through the Outer Hinge, the Left/Right Case, and the Back Brace, holding all three together.

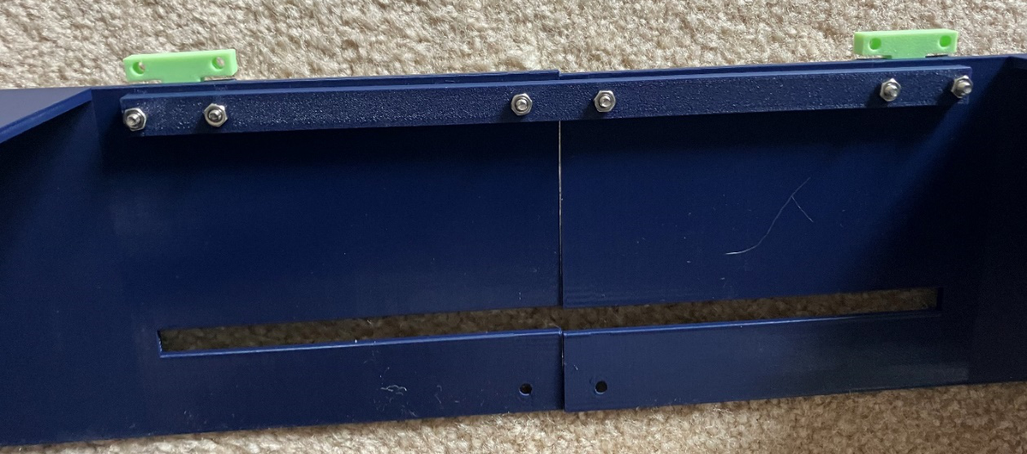
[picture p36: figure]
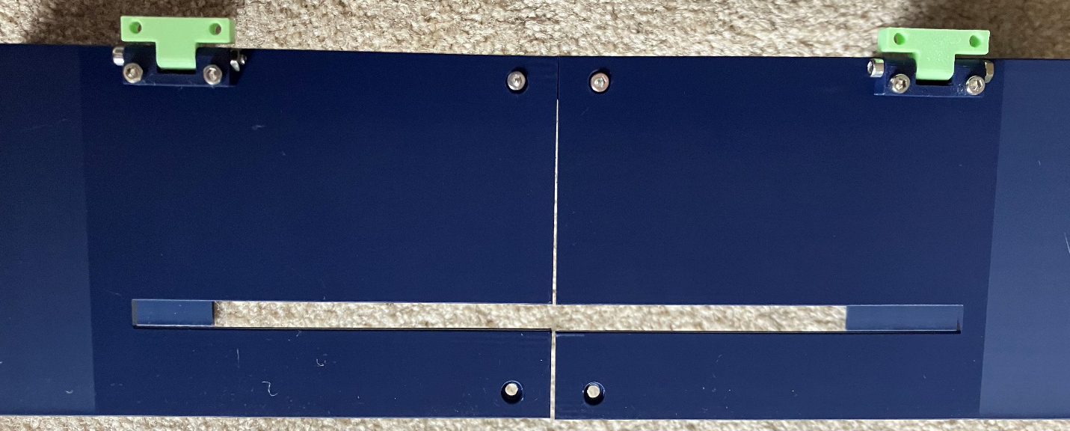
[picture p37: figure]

3. Attach the Lid to the Inner Hinges with four M3x12 screws and four M3 nuts. When the hinges are colinear, the lid should rest on the top surfaces of the case with the cutout on the top of the lid to the right.

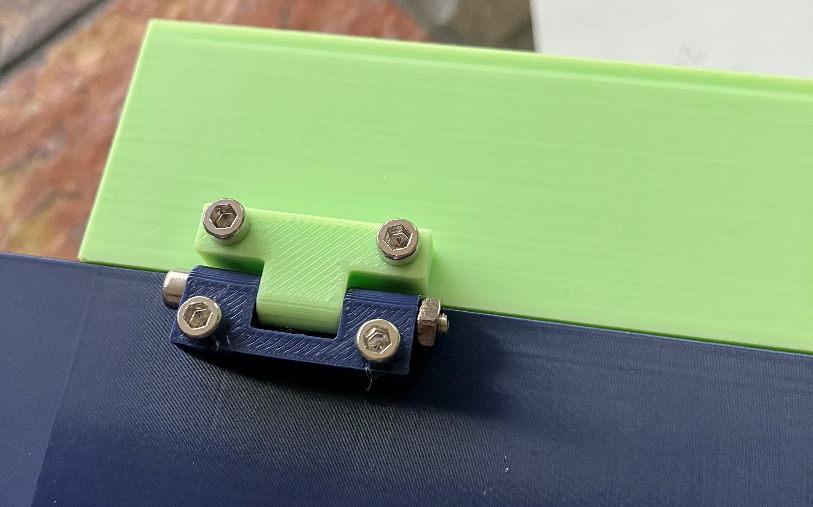
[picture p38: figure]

4. Insert 10 M3 nuts into the ramped holders on the outside edges of the frame. The nuts will not be completely tight in the slots, so don’t flip the embosser over until you’ve screwed on the case or else they’ll all fall out!
5. Set the case onto the frame and screw in 10 M3x6 or M3x8 screw into each of the holes, which will be secured by the nuts inserted in the previous step.

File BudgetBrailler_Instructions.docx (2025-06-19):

BudgetBrailler Instructions

Button Functions from Left to Right

Row 1: Dot 3 Button, Dot 2 Button, Dot 1 Button, Dot 4 Button, Dot 5 Button, Dot 6 Button.

Row 2: Line Up Button, Line Down Button, Home Button, Print Button, No Function, Backspace Button.

Row 3: Space Button, Space Button

Turning on the Brailler

1. Plug in keyboard at the back left of the brailler, ensuring pins are in the correct orientation. This will depend on what kind of connectors you used.
2. Plug in the power supply to the round barrel jack at the back left of the brailler.
3. Listen for a beep from the buzzer and wait for it to stop. This indicates that the brailler is ready.

Feeding Paper

1. Push paper in from the from front of the brailler on top of and parallel to the flat surface with the embossing channel on it.
2. Once the paper contacts the rollers, press the Line Down Button. Repeat pressing the Line Down Button until the location on the paper where you want to start printing is above the embossing channel. Press the Line Up Button to move the paper back out the front of the brailler if you feed the paper too far or need to restart because the paper is crooked.

Navigating on the Page

1. Press the Home Button if necessary to return the carriage to the beginning of the line. This will also delete all the characters you currently have typed but not printed.
2. Press the Line Up Button to go up a line on the page, feeding the paper out of the back of the brailler.
3. Press the Line Down Button to go down a line on the page, feeding the paper out of the front of the brailler.

Typing Braille

Note: Characters cannot be typed while the brailler is taking another action, such printing, homing, or moving the paper. If one of these actions is started, wait for the buzzer in the brailler to stop to indicated that the brailler is ready again.

1. At the same time, press all the Dot Buttons which correspond to the character you wish to type then release them all. Press one or both Space Buttons and none of the Dot Buttons for an empty cell.
2. Press the Backspace Button delete the last character typed. This will not allow you to go passed the last printed character if the Print Buffer Button was used or the beginning of the line if the Print Buffer Button was not used.
3. Press the Print Buffer Button to print all the characters you have typed or type a complete line of 28 characters and the brailler will automatically print the whole line.

Jost Strnat 2025

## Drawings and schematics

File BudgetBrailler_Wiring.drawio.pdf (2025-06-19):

# BudgetBrailler Wiring Diagram

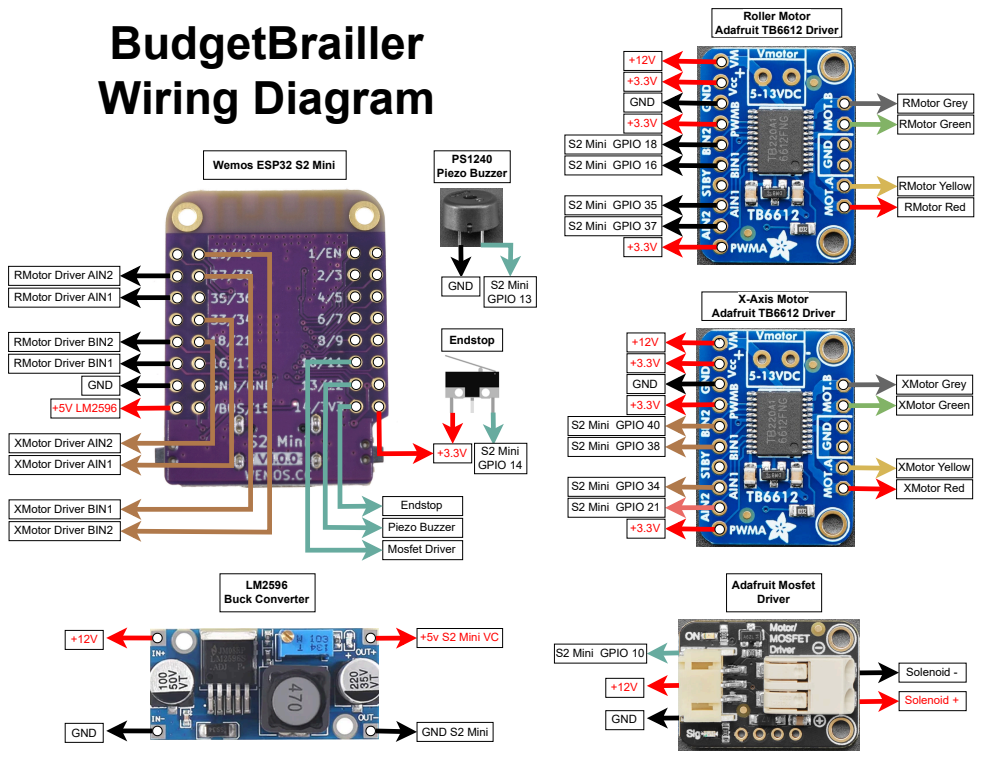
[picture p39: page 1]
GND; +5v S2 Mini VC; GND S2 Mini; Solenoid +; Solenoid -; S2 Mini GPIO 10; RMotor Grey; RMotor Green; RMotor Yellow; RMotor Red; XMotor Grey; XMotor Green; XMotor Yellow; XMotor Red; S2 Mini GPIO 18; S2 Mini GPIO 16; S2 Mini GPIO 37; S2 Mini GPIO 35; Roller Motor Adafruit TB6612 Driver; X-Axis Motor Adafruit TB6612 Driver; Wemos ESP32 S2 Mini; Adafruit Mosfet Driver; LM2596 Buck Converter; S2 Mini GPIO 40; S2 Mini GPIO 38; S2 Mini GPIO 21; S2 Mini GPIO 34; RMotor Driver BIN1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

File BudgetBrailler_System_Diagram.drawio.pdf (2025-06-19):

# BudgetBrailler System Diagram

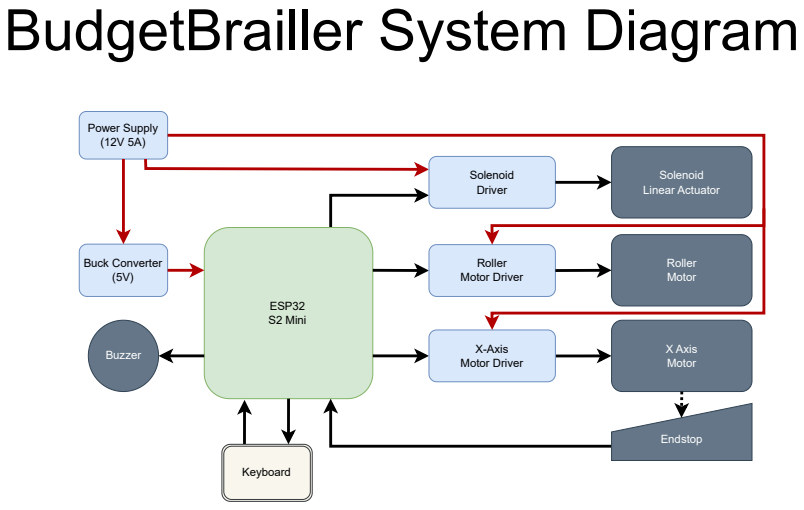
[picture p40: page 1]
ESP32 S2 Mini; Roller Motor Driver; X-Axis Motor Driver; Roller Motor; X Axis Motor Buzzer; Endstop; Buck Converter (5V); Solenoid Linear Actuator; Keyboard; Power Supply (12V 5A); Solenoid Driver

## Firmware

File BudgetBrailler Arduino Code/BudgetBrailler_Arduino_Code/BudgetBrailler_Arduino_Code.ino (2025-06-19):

//BudgetBrailler V1.0 Arduino Code
//By Jost Strnat
//
//libraries to include
  #include <Stepper.h>
//set up stepper motors
  const int stepsPerRevolution = 200;//number of steps per turn of stepper motor

  const int RMotorAin1 = 35;//pin leanding to RMotor driver Ain1 pin
  const int RMotorAin2 = 37;//pin leanding to RMotor driver Ain2 pin
  const int RMotorBin1 = 16;//pin leanding to RMotor driver Bin1 pin
  const int RMotorBin2 = 18;//pin leanding to RMotor driver Bin2 pin

  const int XMotorAin1 = 34;//pin leanding to XMotor driver Ain1 pin
  const int XMotorAin2 = 21;//pin leanding to XMotor driver Ain2 pin
  const int XMotorBin1 = 38;//pin leanding to XMotor driver Bin1 pin
  const int XMotorBin2 = 40;//pin leanding to XMotor driver Bin2 pin

  const int XMotorSpeed = 120;//speed in RPM for XMotor
  const int RMotorSpeed = 120;//speed in RPM for RMotor
  Stepper RMotor(stepsPerRevolution, RMotorAin1, RMotorAin2, RMotorBin1, RMotorBin2);//stepper motor to move toolhead on rail
  Stepper XMotor(stepsPerRevolution, XMotorAin1, XMotorAin2, XMotorBin1, XMotorBin2);//stepper motor for rollers to move paper
  const int motorDelayTime = 0;//a delay after each time the motor moves. Left in but at 0ms for troubleshooting purposes, could cause problems interrupting other processes down the line due to delay function
//other pinouts
  const int laPin = 10;//output pin to transistor controlling linear actuator (LA)
  const int pbPin = 13;//output pin to piezo buzzer (PB)
  const int esPin = 14;//input pin from x endstop (ES)

//keyboard setup variables
  const int numKeys=13;
  const int numColumns=6;
  const int numRows=3;
  const int outputKeyPins[numColumns] = {3,5,7,9,11,12};
    //Output key to column 1 (buttons 1, 7, and space)
    //Output key to column 2 (buttons 2, 8)
    //Output key to column 3 (buttons 3, 9)
    //Output key to column 4 (buttons 4, 10)
    //Output key to column 5 (buttons 5, 11)
    //Output key to column 6 (buttons 6, 12)
  const int inputKeyPins[numColumns] = {2,4,6};
    //Input key from row 1 (buttons 1-6)
    //Input key from row 2 (buttons 7-12)
    //Input key from row 3 (only space key)

  const int keyPinR1[6] = {0,1,2,3,4,5};//button numbers in row 1
  const int keyPinR2[6] = {6,7,8,9,10,11};//button numbers in row 2
  const int keyPinR3[1] = {12};//button numbers in row 3

  bool ButtonsPressed[13];//for converting digital KeyVal reads to which button is pressed, 0 if button not pressed, 1 if button pressed
    const int dot1ButtonPressed = 0;
    const int dot2ButtonPressed = 1;
    const int dot3ButtonPressed = 2;
    const int dot4ButtonPressed = 3;
    const int dot5ButtonPressed = 4;
    const int dot6ButtonPressed = 5;
    const int lineUpButtonPressed = 6;
    const int lineDownButtonPressed = 7;
    const int homeButtonPressed = 8;
    const int printBufferButtonPressed = 9;
    //const int unused2ButtonPressed = 10;
    const int backspaceButtonPressed = 11;
    const int spaceButtonPressed = 12;
  bool ButtonBuffer[13];//Tracks which buttons have been pressed while at least one button is pressed
  bool previousKeyState = 0;//Whether buttons any buttons were pressed (1) or none pressed (0) in previous voidLoop. Used to track if keys have been held down, in which case it should not register as a second instance of typing a character
  bool currentKeyState = 0;//Whether buttons any buttons were pressed (1) or none pressed (0) in the current voidLoop. Holds state until end of void loop until transfered to previousKeyState
  const int buttonPressDelay = 0;//used if you want to pause after reading a button. used for troubleshooting
  unsigned long ButtonPressTimer = 0;//used to track how long a button has been pressed
  bool anyButtonPressed = 0;//used to store if any button is pressed
//cell dot dimension variables
  const float StepsPerMMX = 5;//steps needed to move toolhead 1 mm in the x direction
  const float StepsPerMMR = -4.17;//steps needed to move paper 1mm in the r direction  
  const float DotSpace = 2.34;//mm between dots in a cell 2.34 standard
  const float CellXSpace = 6.2;//mm between corresponding dots in adjacent cells in the same line 6.2 standard
  const float CellRSpace = 10;//mm between corresponding dots in corresponding cells on different lines 10 std 
  const int DotStepsR = round(-10);//number of steps the stepper motor should move in the r direction between first and second dots in a cell
  const int DotStepsR2 = (DotStepsR-2);//number of steps the stepper motor should move in the r direction between second and third dots in a cell, different from DotStepsR due to backlacksh I think
  const int DotStepsX = round(-12);//number of steps the stepper motor should move in the x direction between dots in a cell
  const int CellStepsR = round(CellRSpace*StepsPerMMR);//number of steps the stepper motor should move in the roller direction between cells
  const int CellStepsX = round((CellXSpace-DotSpace)*StepsPerMMR);//number of steps the stepper motor should move in the x direction between cells
//variables about tracking where on the page is being printed
  int LineNumber = 0;//current line number
  int CharNumber = 0;//current character number on current line
  int charStartNum = 0;//used to track last printed character if less than a whole line is printed, also prevents backspacing past this character
  const int CharPerLine = 27;//max characters per line
  const int NumberofLines = 999;//place holder for now
  bool Dot1Buffer[CharPerLine+1];//buffer of button presses corresponding to each character in a line
  bool Dot2Buffer[CharPerLine+1];//buffer of button presses corresponding to each character in a line
  bool Dot3Buffer[CharPerLine+1];//buffer of button presses corresponding to each character in a line
  bool Dot4Buffer[CharPerLine+1];//buffer of button presses corresponding to each character in a line
  bool Dot5Buffer[CharPerLine+1];//buffer of button presses corresponding to each character in a line
  bool Dot6Buffer[CharPerLine+1];//buffer of button presses corresponding to each character in a line
//piezo buffer variables
  const int pbHz = 440;//Hz of piezo buzzer sound for end of line
  const int pbTime = 250;//time in ms the buzzer will sound
//linear actuator variables
  const int laDelayTime = 100;//delay between sending current to LA 
//home variables
  const int HomeTimeoutTime = 3000;//timeout for home to prevent infinitely ramming the endstop if it fails
  unsigned long HomeTimer = 0;//for starting millis timer to timeout home function
//
//
//
//setup sets pinmodes and motor speed
void setup() {
  //start serial communcation for troubleshooting
    Serial.begin(115200);
    delay(2000);
    Serial.println("BeginVoidSetup");
  //set keyboard column pins to Output
  for (int i=0; i < numColumns; i++){
    pinMode(outputKeyPins[i], OUTPUT);
    }
  //set keyboard row pins to Input and use internal pulldown resistors
  for (int i=0; i < numRows; i++){
    pinMode(inputKeyPins[i], INPUT_PULLDOWN);
    }
  //set pinModes for linear actuator, endstop, and piezo buzzer
    pinMode(laPin, OUTPUT);//linear actuator activation pin
    pinMode(esPin, INPUT_PULLDOWN);//end stop pin
    pinMode(pbPin, OUTPUT);//end piezo buzzer

  //set motor speeds
    XMotor.setSpeed(XMotorSpeed);//set x motor speed in rpm
    RMotor.setSpeed(RMotorSpeed);//set r motor speed in rpm
  //beep buzzer to let user know the brailler is ready for typing
    tone(pbPin,pbHz,pbTime);//play a piezzo buzzer tone to indicate the brailler has turned on
    noTone(pbPin);//turn of piezo buzzer
  Serial.println("EndVoidSetup");
}
//core of the script, checks what buttons are pressed, if buttons were pressed tracks until user releases all the keys, then does the actions of the keys that were pressed
void loop() {
  //print commands for troubleshooting
  Serial.println("BeginVoidLoop");
  Serial.println();
    Serial.println("ButtonsPressed");  
    for (int i = 0; i < numKeys; i++){
    Serial.print(ButtonsPressed[i]);
    }
    Serial.println();
    Serial.println("ButtonBuffer");  
    for (int i = 0; i < numKeys; i++){
    Serial.print(ButtonBuffer[i]);
    }
    Serial.println();
  //read keys thengo through each key in the ButtonsPressed[] short term storage array. If any button is pressed, set the variable anyButtonPressed to 1
  FunctionKeyboardRead();  
  anyButtonPressed = 0;
  for(int i = 0; i < numKeys; i++){
    if(ButtonsPressed[i] == 1){
      anyButtonPressed = 1;
    }
    else{
    }
  }
  //if a button is pressed and previously no button was pressed then print for troubleshooting purposes otherwise do nothing and go to non-if end of void loop actions
  if (anyButtonPressed == 1){
    // Serial.println("Button Pressed");
    currentKeyState = 1;
    if(previousKeyState == 0){
      Serial.println("New Button Pressed");
      ButtonPressTimer = millis();//unused timer of how long buttons pressed in case needed later
      delay(buttonPressDelay);//delay used for troubleshooting
    }
    else{}
  }
    //logic for what to do if multiple buttons pressed needs to be added here
    else{//if no buttons were pressed (anyButtonPressed == 0) go through each of the buttons and do the corresponding action if the button was pressed
      currentKeyState = 0;
      if (previousKeyState == 1){
              Serial.println("DOING SOMETHINGGGGGGGGGG");
        if (ButtonBuffer[homeButtonPressed] == 1){//Home x axis
          Serial.println("Home Pressed");
          FunctionHome();
        }
        if (ButtonBuffer[lineDownButtonPressed] == 1){//Move paper out by one line
          Serial.println("LD Pressed");
          FunctionNextLine();
        }
        if (ButtonBuffer[lineUpButtonPressed] == 1){//move paper in by one line
          Serial.println("LU Pressed");
          FunctionPreviousLine();
        }
        if (ButtonBuffer[printBufferButtonPressed] == 1){//print buffer
          Serial.println("PB Pressed");
          FunctionPrintBuffer();
        }  
        // if (){//unused button
        //   delay(0);
        // }    
        if (ButtonBuffer[backspaceButtonPressed] == 1){//backspace
          Serial.println("BS Pressed");
          FunctionBackspace();
        }  
        //if any of the 6 dot buttons or space was pressed, then add a character to the buffer using FunctionAddToBuffer 
          //if the max characters in the line has been reached, print buffer and carraige return 
        if (ButtonBuffer[dot1ButtonPressed] == 1 || ButtonBuffer[dot2ButtonPressed] == 1 || ButtonBuffer[dot3ButtonPressed] == 1 || 
            ButtonBuffer[dot4ButtonPressed] == 1 || ButtonBuffer[dot5ButtonPressed] == 1 || ButtonBuffer[dot6ButtonPressed] == 1 || 
            ButtonBuffer[spaceButtonPressed] == 1){
          Serial.print("TypeButtonsPressed");
          FunctionAddToBuffer();
              if(CharNumber > CharPerLine){
                FunctionPrintBuffer();
                FunctionNextLine();
                FunctionHome();
            }
          }
        }
        //after completing actions, wipe short term tracking of buttons that were pressed
        FunctionResetButtons();
      }
  //non-if end of void loop actions, track whether a key was pressed in the current cycle so it can be reference in the next cycle
  previousKeyState = currentKeyState;
}
//FunctionNextLine pushes the paper out the front of the the brailler (moves the print line down on the page from the reader's perspective)
  //LineNumber is tracked but not currently used
void FunctionNextLine(){
  Serial.println("FunctionNextLine");
  RMotor.step(-CellStepsR);
  LineNumber++;
  FunctionBacklashAdjust();
}
//FunctionPreviousLine pushes the paper out the back of the the brailler (moves the print line up on the page from the reader's perspective)
  //LineNumber is tracked but not currently used
void FunctionPreviousLine(){
  Serial.println("FunctionPreviousLine");
  RMotor.step(CellStepsR);
  LineNumber--;
  FunctionBacklashAdjust();
}
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

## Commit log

2025-05-09 Added solidworks files
    [BB_Back_Brace.SLDPRT, BB_Belt_Clamp.SLDPRT, BB_CB_Mount.SLDPRT, BB_Cam_Latch.SLDPRT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]
2025-05-09 Add files via upload
    Added draft wiring, BoM, instructions
    [BTW_V0.2_BoM.xlsx]
2025-05-09 Add files via upload
    Added arduino code
2025-05-09 Added assembly STEP file
2025-06-15 Delete BTW_V0.2_BoM.xlsx
    Removed outdated BoM
    [BTW_V0.2_BoM.xlsx]
2025-06-15 Added Files
    Added BoM, system diagram, wiring diagram
    [Budget_Brailler_BoM.xlsx]
2025-06-15 Delete BTW_V0.2 Wiring.pptx
    Removed outdated wiring
2025-06-15 Add files via upload
    Added updated Arduino Code
2025-06-19 Add files via upload
    Updated CAD files
    [BB_Channel.SLDPRT, BB_Left_Casing.SLDPRT, BB_Left_Side.SLDPRT, BB_Middle.SLDPRT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]
2025-06-19 Add files via upload
    Added Keyboard files
    [BB_Keyboard_Bottom.SLDPRT, BB_Keyboard_Bottom.STL, BB_Keyboard_Top.SLDPRT, BB_Keyboard_Top.STL]
2025-06-19 Add files via upload
    Added slightly outdated assembly instructions and new keyboard functions
2025-06-19 Add files via upload
    Added STLs
    [BB_Back_Brace.STL, BB_Belt_Clamp.STL, BB_CB_Mount.STL, BB_Cam_Latch.STL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]
